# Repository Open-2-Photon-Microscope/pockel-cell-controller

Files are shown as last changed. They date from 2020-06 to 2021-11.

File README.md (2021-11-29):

# Pockel cell controller

An open source circuit to modulate laser intensity in a 2 Photon microscope. This modulation is necessary when visual stimulation is used to elicit responses from biological tissue (photoreceptors). The laser power is tunned high and low periodically (in our systems at 500Hz using a square wavefom at 80% duty cycle). When laser power is low, visual stimulation is on, when laser power is high, visual stimulation is off. 

This driver was built to control a laser modulator from Conoptics. Specifically [his model](https://www.lambdaphoto.co.uk/electro-optic-modulator-systems.html).

The main purpose of this circuit is to condition an analog signal using an fast switch IC that opens and closes the analog line using a digital 0-5V square signal (0V circuit open, 5V circuit closed). The original switching signal is 1.6ms at 5V and 0.4ms at 0V (composing a 500Hz signal), but other signals can be used.



This board can take an internal analog signal, where the signal amplitude (and therefore the laser intensity) is set by a potentiometer, or an external signal connected via a BNC cable.
 
The Pockels' cell driver was inspired by earlier devices designed and built by R. Berndt ([HIH Tübingen](<https://www.hih-tuebingen.de/en/>)), part of a project of [T. Euler's lab](<http://www.eye-tuebingen.de/eulerlab/>).

## To do:
1. Link board to KitSpace

## History:

v2.0
- Document, add licenses to the repository (A. Maia Chagas)
- KiCad designs updated to KiCad 5 (A. Maia Chagas)
- Designs of the board updated; ported to KiCad (F. Janiak)

V1.0
 - Pockels' cell driver design by R. Berndt ([HIH Tübingen](<https://www.hih-tuebingen.de/en/>)) and [T. Euler's lab](<http://www.eye-tuebingen.de/eulerlab/>).

--- 

Footprints for KiCad downloaded from [ultralibrarian](<https://app.ultralibrarian.com>).

- [CA3240](<https://app.ultralibrarian.com/details/f0fe15b2-106c-11e9-ab3a-0a3560a4cccc/Intersil/CA3240AE?uid=155cdc561030ca9b&exports=KiCAD>)
- [LM10CLN](<https://app.ultralibrarian.com/details/49f2f7e6-1073-11e9-ab3a-0a3560a4cccc/Texas-Instruments/LM10CLN?uid=6d97a49d38e0b250&exports=KiCAD>)

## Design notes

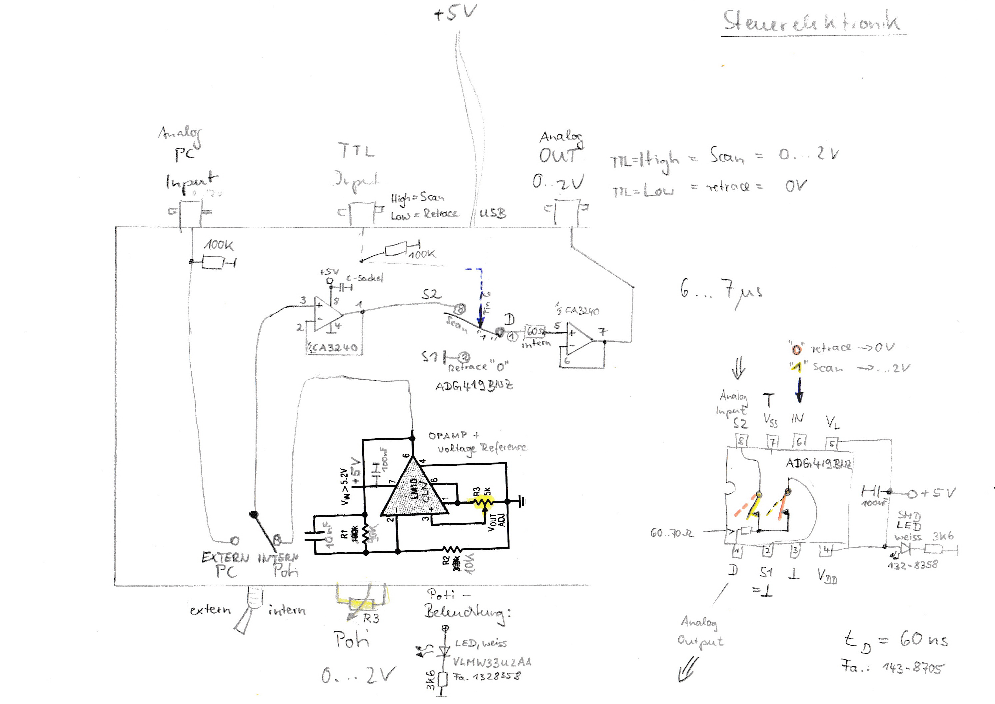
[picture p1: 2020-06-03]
media/Berndt_design.jpg

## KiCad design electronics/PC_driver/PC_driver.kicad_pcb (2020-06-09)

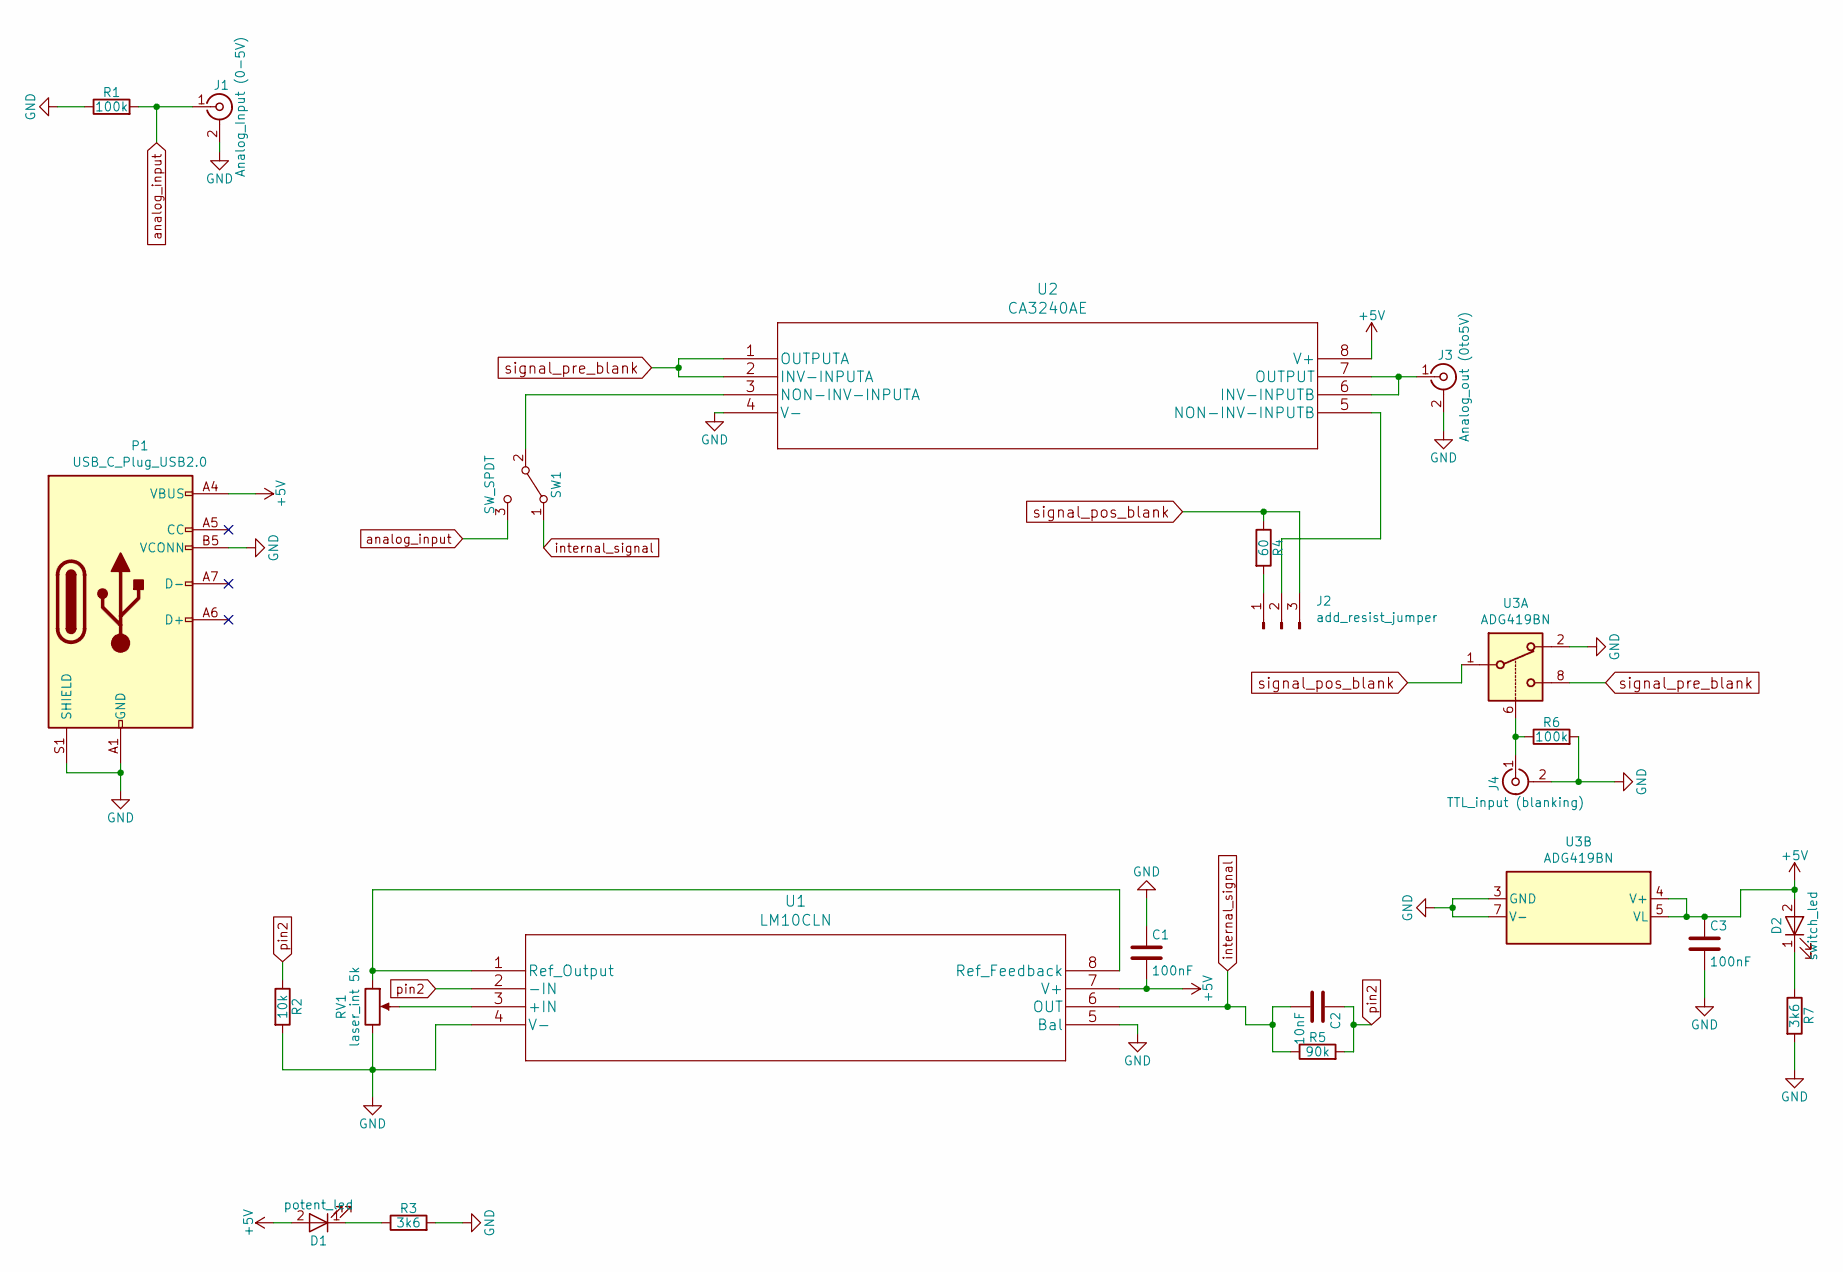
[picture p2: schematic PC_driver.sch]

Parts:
C1, C3: 100nF; C_Disc_D5.0mm_W2.5mm_P2.50mm
C2: 10nF; C_Disc_D5.0mm_W2.5mm_P2.50mm
D1: potent_led; LED_D5.0mm_Clear
D2: switch_led; LED_D5.0mm_Clear
J1: Analog_Input (0-5V); BNC_Amphenol_B6252HB-NPP3G-50_Horizontal
J2: add_resist_jumper; PinHeader_1x03_P2.54mm_Vertical
J3: Analog_out (0to5V); BNC_Amphenol_B6252HB-NPP3G-50_Horizontal
J4: TTL_input (blanking); BNC_Amphenol_B6252HB-NPP3G-50_Horizontal
P1: USB_C_Plug_USB2.0; USB_C_Receptacle_GCT_USB4085
R1, R6: 100k; R_Axial_DIN0309_L9.0mm_D3.2mm_P12.70mm_Horizontal
R2: 10k; R_Axial_DIN0309_L9.0mm_D3.2mm_P12.70mm_Horizontal
R3, R7: 3k6; R_Axial_DIN0309_L9.0mm_D3.2mm_P12.70mm_Horizontal
R4: 60; R_Axial_DIN0309_L9.0mm_D3.2mm_P12.70mm_Horizontal
R5: 90k; R_Axial_DIN0309_L9.0mm_D3.2mm_P12.70mm_Horizontal
RV1: laser_int 5k; Potentiometer_ACP_CA14-H5_Horizontal
SW1: SW_SPDT; SW_E-Switch_EG1224_SPDT_Angled
U1: LM10CLN; DIP-8_W7.62mm
U2: CA3240AE; DIP-8_W7.62mm
U3: ADG419BN; DIP-8_W7.62mm

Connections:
+5V: C1.2, C3.1, D1.2 (A), D2.2 (A), P1.A4 (VBUS), P1.A9 (VBUS), P1.B4 (VBUS), P1.B9 (VBUS), U1.7 (V+), U2.8 (V+), U3.4 (V+), U3.5 (VL)
GND: C1.1, C3.2, J1.2 (Ext), J3.2 (Ext), J4.2 (Ext), P1.A1 (GND), P1.A12 (GND), P1.B1 (GND), P1.B5 (VCONN), P1.B12 (GND), P1.S1 (SHIELD), R1.1, R2.2, R3.2, R6.2, R7.2, RV1.3, U1.4 (V-), U1.5 (Bal), U2.4 (V-), U3.2, U3.3 (GND), U3.7 (V-)
unnamed: D1.1 (K), R3.1
unnamed: D2.1 (K), R7.1
unnamed: J2.1, R4.2
unnamed: J2.2, U2.5 (NON-INV-INPUTB)
unnamed: J3.1 (In), U2.6 (INV-INPUTB), U2.7 (OUTPUT)
unnamed: J4.1 (In), R6.1, U3.6
unnamed: RV1.1, U1.1 (Ref_Output), U1.8 (Ref_Feedback)
unnamed: RV1.2, U1.3 (+IN)
unnamed: SW1.2 (B), U2.3 (NON-INV-INPUTA)
analog_input: J1.1 (In), R1.2, SW1.3 (C)
internal_signal: C2.2, R5.1, SW1.1 (A), U1.6 (OUT)
pin2: C2.1, R2.1, R5.2, U1.2 (-IN)
signal_pos_blank: J2.3, R4.1, U3.1
signal_pre_blank: U2.1 (OUTPUTA), U2.2 (INV-INPUTA), U3.8

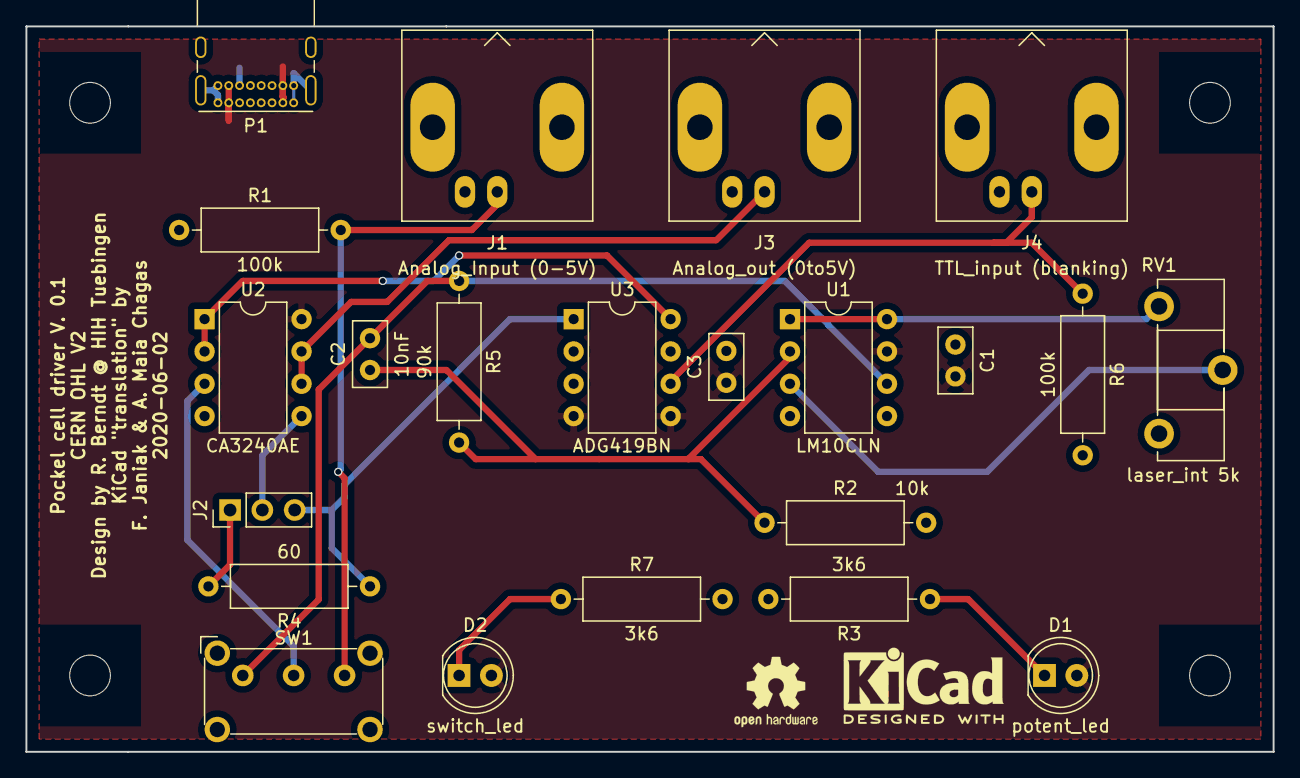
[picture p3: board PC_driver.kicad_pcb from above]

Board: 2 copper layers, 98.0 x 57.0 mm, 22 parts (0 on the bottom side), 16 nets.

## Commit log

2020-03-06 filip's first implementation using KiCad4
    [PC_driver-2020-03-06-10-49-16.sch, PC_driver-B.Cu.gbr, PC_driver-B.Mask.gbr, PC_driver-B.SilkS.gbr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]
2020-03-06 restart, some parts are available in kicad 5
    [PC_driver-2020-03-06-10-49-16.sch, PC_driver-B.Cu.gbr, PC_driver-B.Mask.gbr, PC_driver-B.SilkS.gbr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]
2020-03-06 update components
    [PC_driver-2020-03-06-14-06-08.sch, PC_driver-B.Cu.gbr, PC_driver-B.Mask.gbr, PC_driver-B.SilkS.gbr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]
2020-06-01 update board
    [PC_driver.sch, pockel_cell_driver.kicad_pcb, pockel_cell_driver.sch]
2020-06-01 fix labels and buggy resistor
    [PC_driver.sch]
2020-06-01 finished schmatics and footprint association
    [PC_driver-2020-03-06-10-49-16.sch, PC_driver-B.Cu.gbr, PC_driver-B.Mask.gbr, PC_driver-B.SilkS.gbr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]
2020-06-02 finish part placement, wiring and plotting
    [PC_driver-B_Adhes.gbr, PC_driver-B_CrtYd.gbr, PC_driver-B_Cu.gbr, PC_driver-B_Fab.gbr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]
2020-06-02 correct misspelling
    [PC_driver-B_Adhes.gbr, PC_driver-B_CrtYd.gbr, PC_driver-B_Cu.gbr, PC_driver-B_Fab.gbr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]
2020-06-09 correct bug on board plotting
    [PC_driver-B.Cu.gbr, PC_driver-B.Mask.gbr, PC_driver-B.SilkS.gbr, PC_driver-B_Adhes.gbr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]
2020-06-09 update readme with details of the laser modulator being used

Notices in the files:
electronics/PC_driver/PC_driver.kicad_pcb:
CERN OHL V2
